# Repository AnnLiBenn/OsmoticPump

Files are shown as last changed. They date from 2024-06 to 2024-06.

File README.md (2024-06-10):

# Osmotic Pump Backpack Parts List and Instructions

Both .stl and .sldprt files have been included for your convinence. All SLDPRT files were made on SOLIDWORKS 2022.

This backpack was designed for use with [ALZET Brain Infusion Kit 3](https://www.alzet.com/brain-infusion-kit/alzet-brain-infusion-kits/).

## Osmotic Pump Backpack Parts List

In this repository are all the parts required to build an osmotic pump backpack. It is made for use with ALZET Micro Osmotic Pumps. All parts were printed on FormLabs Form 3+.

### Backpack

This is the main body of the backpack that houses two osmotic pumps. Print in Durable resin at 0.8 density and 0.45mm touchpoints.

<p align="center">
Screenshot 2024-06-10 at 10 47 44 AM
</p>

### Cap

This is the cap of the backpack. It connects to the steel tubing for the catheter tubing, and has a central hole for topping off ACSF. Print in Durable resin at 0.8 density and 0.45 touchpoints.

<p align="center">
Screenshot 2024-06-10 at 10 50 05 AM
</p>

# Assembly Instructions

## Preparing the Osmotic Pumps

<p align="center">

</p>

**Pre-prep:**

- **Prepare the cannula:** Shave down two opposing halves of a cannula and use epoxy to combine them, such that the catheter tubing is approximatly 1mm apart.
<p align="center">


</p>
  
- **Prepare catheter tubing:** Cut tubing to approx 1.5in
- **Prepare the filling syringe:** Using an angled blunt syringe, attach catheter tubing to the syringe, then the stainless steel tube to the end of the catheter tubing

**Pump Prep:**

**1.** Remove flow moderators from stainless steel tubes

**2.** Heat 0.9% saline to 37°C

**3.** Remove the cannula from the tubing

**4.** Attach the stainless steel tube to the catheter tubing below the cap, where the catheter tubing covers 3mm of the stainless steel tube 
<p align="center">

</p>

**5.** Prepare ACSF

**6.** One catheter tube at a time, insert the stainless steel tube of the filling syringe into the distal end of the catheter

<p align="center">

</p>

**7.** Fill the catheter and the stainless steel tube using the filling syringe

**8.** Leaving the filling syring attached, fill the pump with ACSF using the sterile filling needle:

- Weigh the empty pump (0.35g)
- Fill the pump with 27 guage filling syringe until liquid comes out the top
- Weigh the filled pump (0.45g)
  
**9.** With the filling syring still attached, insert the flow moderator into the pump, ensuring there are no bubbles
  
**10.** Remove the filling syringe and reattach the cannula

**11.** Repeat the same for the othe side

<p align="center">

</p>

**12.** Incubate the pumps (no the caps - keep them dry) in 37°C 0.9% saline

## Preparing the Backpack

1. Cut a length of elastic to go create leg loops in backpacks, inserting either end into the designated holes
2. After placing the backpack on the bird, insert cap into backpack
3. Fill backpack with saline using the middle hole in the cap
4. Seal backpack, middle holes, and steel tubing holes with UV curing silicone sealant
5. Remove silicond plug in middle hole to replenish saline as necessary

<p align="center">

</p>

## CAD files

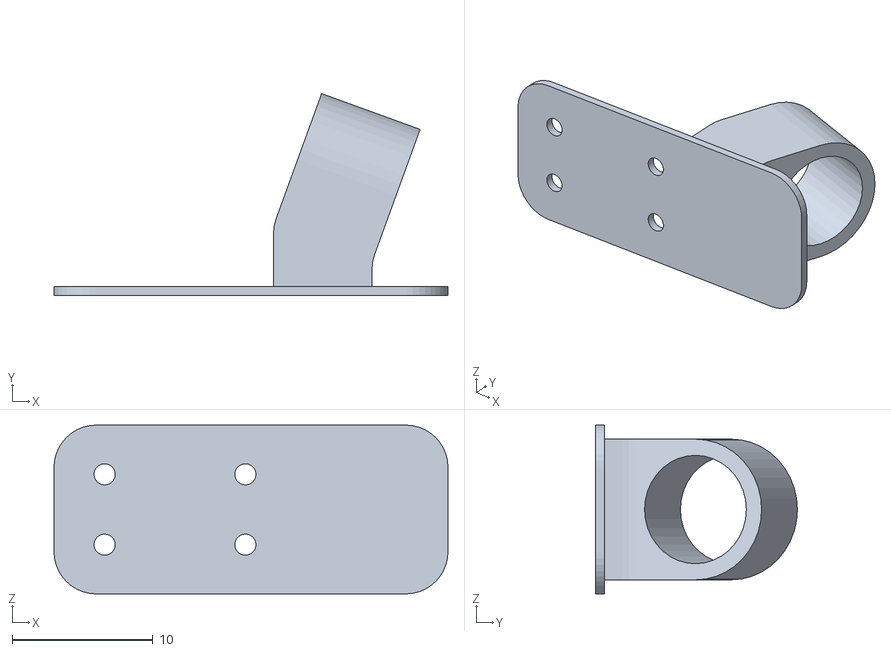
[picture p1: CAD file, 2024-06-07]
PartFiles/OspoticPumpBackpack.STL
28.0 x 14.3 x 12.0

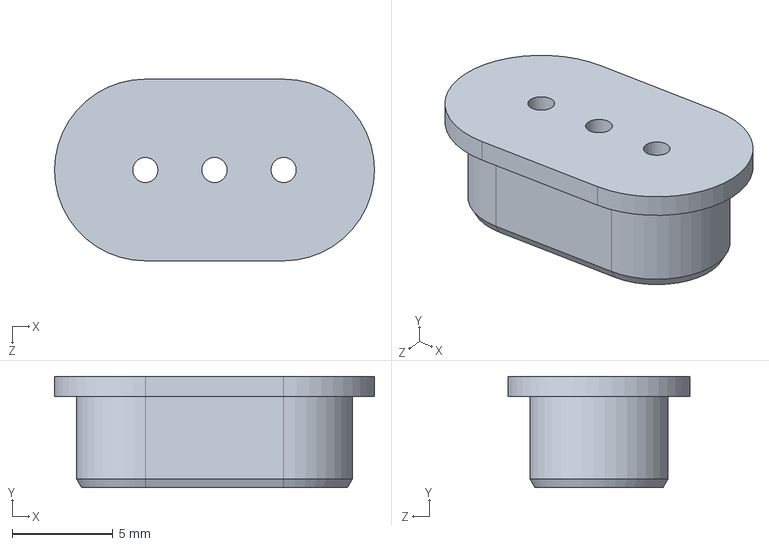
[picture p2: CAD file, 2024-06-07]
PartFiles/PackCap.SLDPRT
15.9 x 5.50 x 9.00 mm

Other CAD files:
PartFiles/OsmpticPumpBackpack.SLDPRT
PartFiles/PackCap.STL
